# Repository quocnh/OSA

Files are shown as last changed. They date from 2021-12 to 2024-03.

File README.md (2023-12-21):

# ESP32_MedicalDevice
IoT devices to collect SPo2 and ECG for cancer treatment.

Downloading Repo from Github
---------------------------------------------------------------------------------------------------------------------------
- 1.) Navigate to "https://github.com/quocnh/OSA_Medical_Devices"
- 2.) Copy HTTPS link
- 3.) Open Git Bash in a local folder
- 4.) enter "git clone <Insert HTTP link here>"
---------------------------------------------------------------------------------------------------------------------------

Installing Firmware to ESP32
---------------------------------------------------------------------------------------------------------------------------
- 1.) Add ESP32 boards to Arduino IDE
	-File -> Preferences 
	-Enter "https://dl.espressif.com/dl/package_esp32_index.json" into "Additional Board Manager URLs" field
	-Tools -> Board -> Boards Manager...
	-Find "esp32" and install version 1.05
- 2.) Add necessary libraries to Arduino IDE
	-Sketch -> Include Library -> Add .ZIP library
	-Select .ZIP from "libraries" folder
	-Repeat for all libraries in the "libraries" folder

   	ArduinoHtppClient (0.5.0)
  	NTPClient(3.2.1)
  	AduinoJson(6.21.4)
  	AutoConnect(1.4.2)
  	PageBuilder(1.5.6)
  	PubSubCleint(2.8)
  	TPBubSupClient(2.9.1)
  	Thingsboard(0.10.2)
  
- 3.) Upload sketch to ESP32
	-Tools -> Board -> ESP32 dev module
	-Tools -> upload speed -> 115200
	-Tools -> Port -> select your COM port
	(https://www.silabs.com/developers/usb-to-uart-bridge-vcp-drivers?tab=downloads) iff missing driver
	-upload (arrow symbol)
	-If connection doesn't work, close sketch, disconnect and reconnect USB, reopen sketch and upload
---------------------------------------------------------------------------------------------------------------------------

Opening Thingsboard Dashboard
---------------------------------------------------------------------------------------------------------------------------
- 1.) Open "http://134.129.97.131:8080/" and sign in
	-login: "tenant@thingsboard.org"
	-password: "tenant"
- 2.) Navigate to ESP32 dashboard
	-Dashboard groups -> ESP32 -> Devkit Test
---------------------------------------------------------------------------------------------------------------------------

WiFi Autoconnect
---------------------------------------------------------------------------------------------------------------------------
- 1.) Power on programmed device and connect to the SpO2ap/ECGap with the default password "12345678"
- 2.) Navigate to "192.168.10.101/_ac" with SpO2ap and "192.168.10.102/_ac" with ECGap on your mobile device's web browser
- 3.) Press settings icon
- 4.) Press menu icon
- 5.) Add wifi network credentials
- 6.) Device will now autoconnect to WiFi
---------------------------------------------------------------------------------------------------------------------------
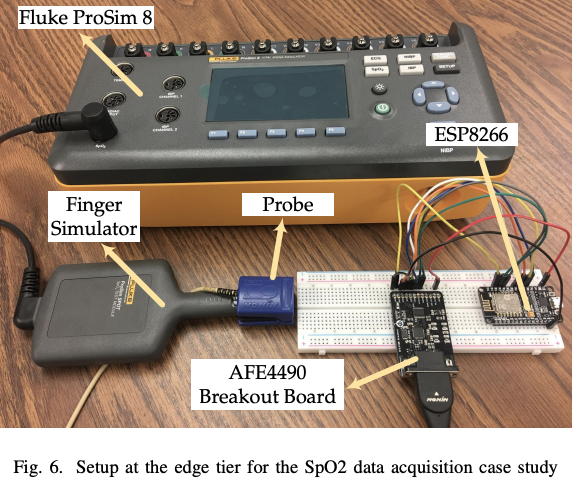
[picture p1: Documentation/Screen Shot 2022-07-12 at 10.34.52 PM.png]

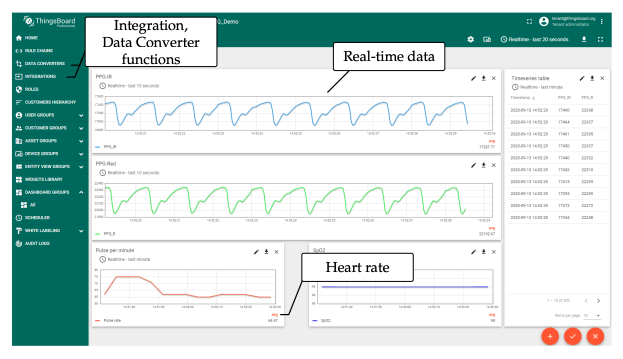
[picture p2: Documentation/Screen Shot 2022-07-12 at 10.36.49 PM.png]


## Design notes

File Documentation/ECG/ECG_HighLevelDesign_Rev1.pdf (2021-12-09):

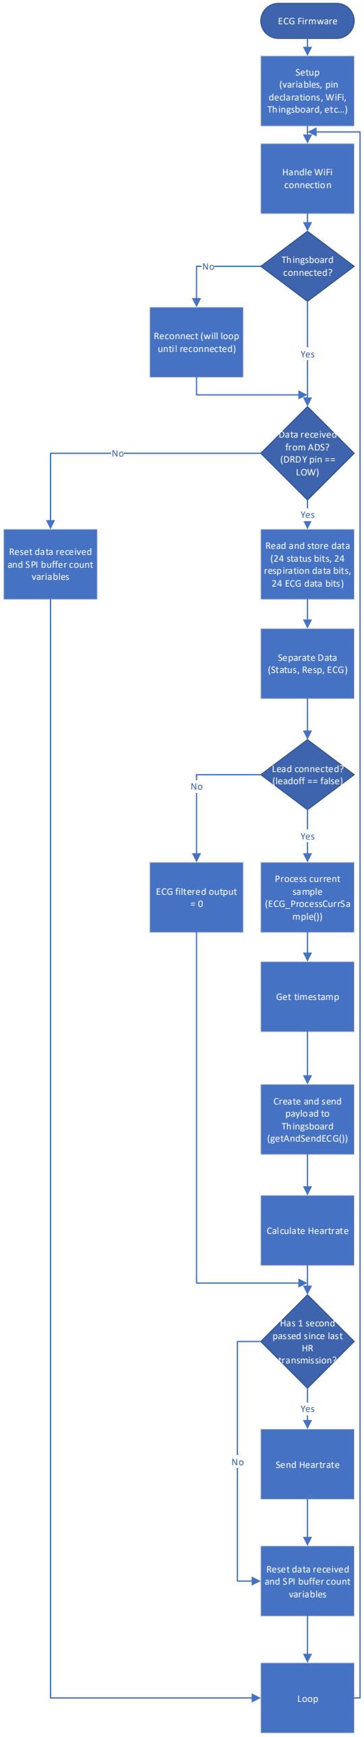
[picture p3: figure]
ECG Firmware; Setup (variables, pin declarations, WiFi, Thingsboard, etc…); Handle WiFi connection; Thingsboard connected?; Reconnect (will loop until reconnected); Data received from ADS? (DRDY pin == LOW); Yes; Read and store data (24 status bits, 24 respiration data bits, 24 ECG data bits); Reset data received and SPI buffer count variables; Separate Data (Status, Resp, ECG); Process current sample (ECG_ProcessCurrSa mple()); Get timestamp; Lead connected? (leadoff == false); Create and send payload to Thingsboard (getAndSendECG()); Calculate Heartrate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

Tom Hoskins – ECG Firmware high-level block diagram Rev 1 Arduino File: ESP32_to_Thingsboard.ino

Important configuration information

Pins:
ADS1292_DRDY_PIN = 4;
ADS1292_CS_PIN = 15;
ADS1292_START_PIN = 0;
ADS1292_PWDN_PIN = 2;

Sampling Rate: 250 SPS

Digital Filter:
40Hz LowPass
161 Order

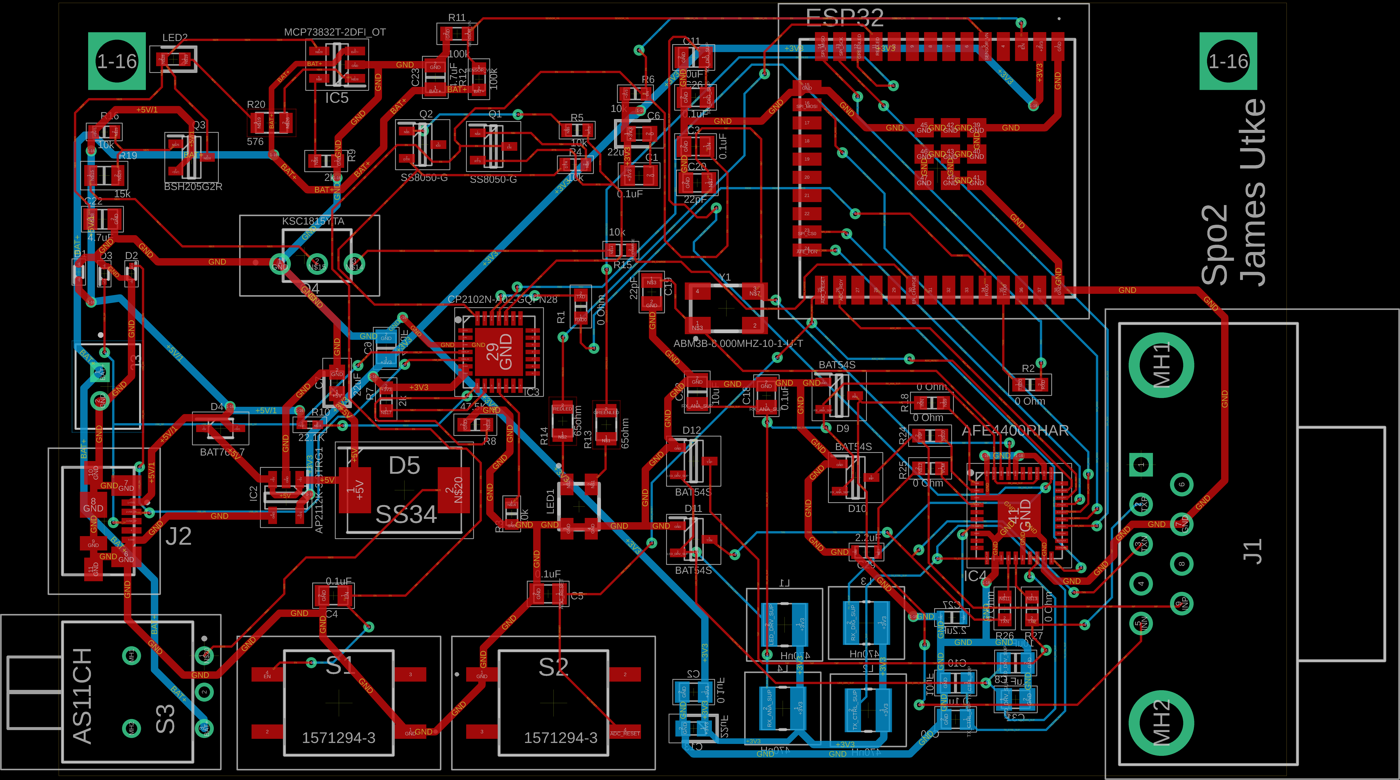
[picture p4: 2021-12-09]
Documentation/SPO2/SPo2_Rev.png

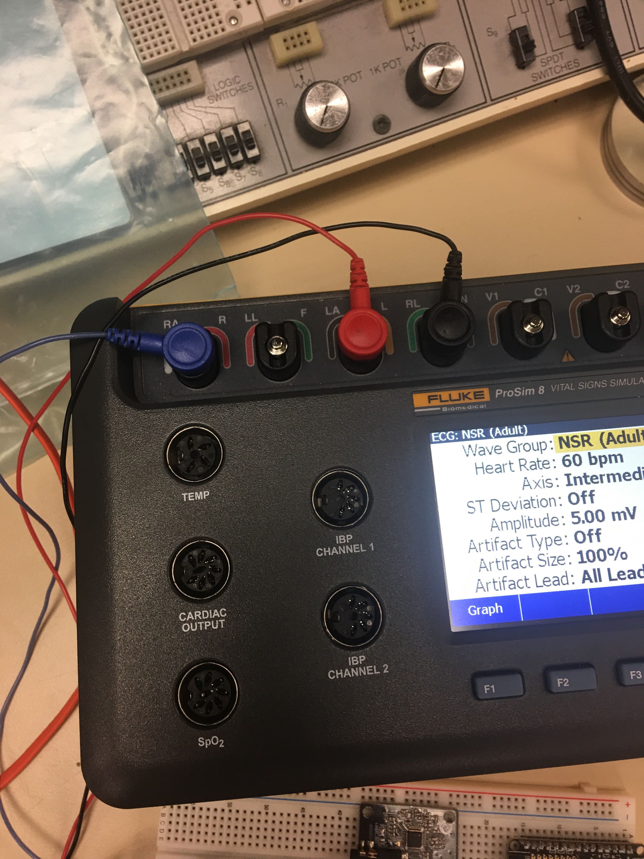
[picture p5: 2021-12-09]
Documentation/ECG/Image from iOS.jpg

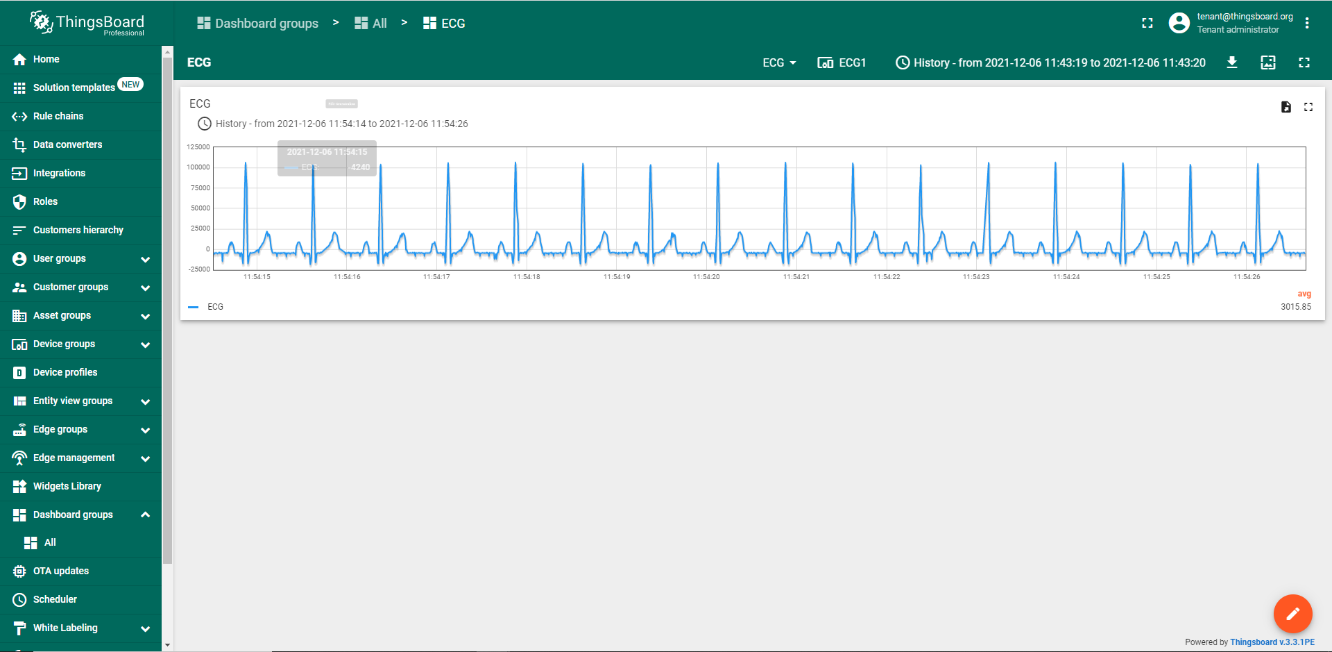
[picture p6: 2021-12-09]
Documentation/image.png

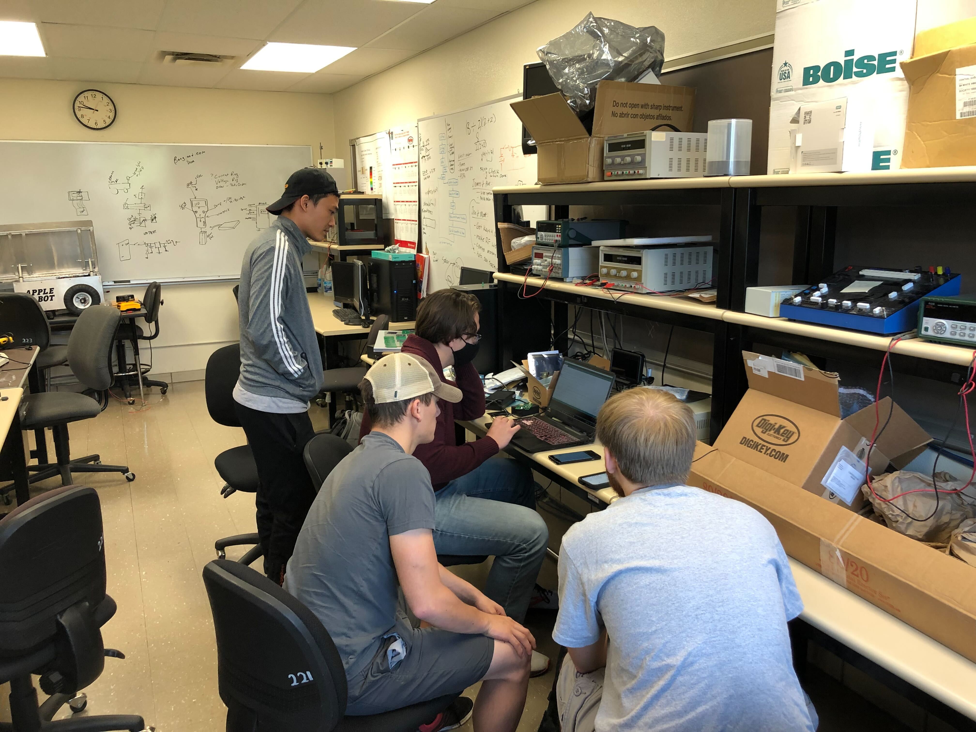
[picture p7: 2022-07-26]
Documentation/team.jpeg

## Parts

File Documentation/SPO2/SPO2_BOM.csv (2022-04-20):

Part | Value | Device | Package | Description | ARROW_PART_NUMBER | ARROW_PRICE-STOCK | DESCRIPTION | DIGI-KEY_PART_NUMBER | HEIGHT | MANUFACTURER_NAME | MANUFACTURER_PART_NUMBER | MF | MOUSER_PART_NUMBER | MOUSER_PRICE-STOCK | MP | PACKAGE | PURCHASE-URL | VALUE
C1 | 0.1uF | C0805C104K5RAC7411 | CAPC2012X88N | Cap Ceramic 0.1uF 50V X7R 10% Pad SMD 0805 125C T/R |  |  | Cap Ceramic 0.1uF 50V X7R 10% Pad SMD 0805 125C T/R |  | 0.88mm | Kemet | C0805C104K5RAC7411 |  | 80-C0805C104K5RACLR | https://www.mouser.co.uk/ProductDetail/KEMET/C0805C104K5RAC7411/?qs=jbRM9o5BbzPcVXF0wW9AYg%3D%3D |  |  |  | 0.1uF
C2 | 0.1uF | C0805C104K5RAC7411 | CAPC2012X88N | Cap Ceramic 0.1uF 50V X7R 10% Pad SMD 0805 125C T/R |  |  | Cap Ceramic 0.1uF 50V X7R 10% Pad SMD 0805 125C T/R |  | 0.88mm | Kemet | C0805C104K5RAC7411 |  | 80-C0805C104K5RACLR | https://www.mouser.co.uk/ProductDetail/KEMET/C0805C104K5RAC7411/?qs=jbRM9o5BbzPcVXF0wW9AYg%3D%3D |  |  |  | 0.1uF
C3 | 0.1uF | C0805C104K5RAC7411 | CAPC2012X88N | Cap Ceramic 0.1uF 50V X7R 10% Pad SMD 0805 125C T/R |  |  | Cap Ceramic 0.1uF 50V X7R 10% Pad SMD 0805 125C T/R |  | 0.88mm | Kemet | C0805C104K5RAC7411 |  | 80-C0805C104K5RACLR | https://www.mouser.co.uk/ProductDetail/KEMET/C0805C104K5RAC7411/?qs=jbRM9o5BbzPcVXF0wW9AYg%3D%3D |  |  |  | 0.1uF
C4 | 0.1uF | C0805C104K5RAC7411 | CAPC2012X88N | Cap Ceramic 0.1uF 50V X7R 10% Pad SMD 0805 125C T/R |  |  | Cap Ceramic 0.1uF 50V X7R 10% Pad SMD 0805 125C T/R |  | 0.88mm | Kemet | C0805C104K5RAC7411 |  | 80-C0805C104K5RACLR | https://www.mouser.co.uk/ProductDetail/KEMET/C0805C104K5RAC7411/?qs=jbRM9o5BbzPcVXF0wW9AYg%3D%3D |  |  |  | 0.1uF
C5 | 0.1uF | C0805C104K5RAC7411 | CAPC2012X88N | Cap Ceramic 0.1uF 50V X7R 10% Pad SMD 0805 125C T/R |  |  | Cap Ceramic 0.1uF 50V X7R 10% Pad SMD 0805 125C T/R |  | 0.88mm | Kemet | C0805C104K5RAC7411 |  | 80-C0805C104K5RACLR | https://www.mouser.co.uk/ProductDetail/KEMET/C0805C104K5RAC7411/?qs=jbRM9o5BbzPcVXF0wW9AYg%3D%3D |  |  |  | 0.1uF
C6 | 22uF | F381A226MMAAXE | CAPPC1609X90N | 22uF F38 Series Conductive Polymer, Miniature, Undertab Solid Electrolytic Chip Capacitors |  |  | 22uF F38 Series Conductive Polymer, Miniature, Undertab Solid Electrolytic Chip Capacitors |  | 0.9mm | AVX | F381A226MMAAXE |  | 581-F381A226MMAAXE | https://www.mouser.co.uk/ProductDetail/AVX/F381A226MMAAXE?qs=gTYE2QTfZfQFi8JvXKXiKg%3D%3D |  |  |  | 22uF
C7 | 22uF | F381A226MMAAXE | CAPPC1609X90N | 22uF F38 Series Conductive Polymer, Miniature, Undertab Solid Electrolytic Chip Capacitors |  |  | 22uF F38 Series Conductive Polymer, Miniature, Undertab Solid Electrolytic Chip Capacitors |  | 0.9mm | AVX | F381A226MMAAXE |  | 581-F381A226MMAAXE | https://www.mouser.co.uk/ProductDetail/AVX/F381A226MMAAXE?qs=gTYE2QTfZfQFi8JvXKXiKg%3D%3D |  |  |  | 22uF
C8 | 10uF | TMK212BC6106KG-T | CAPC2114X145N@1 | Status\tMass Production (Preferred) Capacitance\t10 uF +/- 10 % Case Size (EIA/JIS)\t0805/2012 Rated Voltage\t25 V tan (max)\t10 % Temperature Characteristic (EIA)\tX6S Operating Temp. Range (EIA)\t-55 to +105 High Temperature Loading (% Rated Voltage)\t150 % Insulation Resistance (min)\t100 MuF Dimension L\t2.0 +0.20/-0.00 mm Dimension W\t1.25 +0.20/-0.00 mm Dimension T\t1.25 +0.20/-0.00 mm Dimension e\t0.50 +/-0.25 mm RoHS Compliance (10 subst.)\tYes REACH Compliance (205 subst.)\tYes IEC62474 (Ver. D19 |  |  | Status Mass Production (Preferred) Capacitance 10 uF +/- 10 % Case Size (EIA/JIS) 0805/2012 Rated Voltage 25 V tan (max) 10 % Temperature Characteristic (EIA) X6S Operating Temp. Range (EIA) -55 to +105 High Temperature Loading (% Rated Voltage) 150 % Insulation Resistance (min) 100 MuF Dimension L 2.0 +0.20/-0.00 mm Dimension W 1.25 +0.20/-0.00 mm Dimension T 1.25 +0.20/-0.00 mm Dimension e 0.50 +/-0.25 mm RoHS Compliance (10 subst.) Yes REACH Compliance (205 subst.) Yes IEC62474 (Ver. D19 |  | 1.45mm | TAIYO YUDEN | TMK212BC6106KG-T |  | 963-TMK212BC6106KG-T | https://www.mouser.co.uk/ProductDetail/Taiyo-Yuden/TMK212BC6106KG-T/?qs=rI7uf1IzohRW7kV5WJ6mlg%3D%3D
C9 | 4.7uF | JMK212B7475KGHT | CAPC2114X145N | Taiyo Yuden JMK212B7475KGHT 4.7F MLCC 6.3V dc +/-10% Tolerance SMD |  |  | Taiyo Yuden JMK212B7475KGHT 4.7F MLCC 6.3V dc +/-10% Tolerance SMD |  | 1.45mm | TAIYO YUDEN | JMK212B7475KGHT |  | 963-JMK212B7475KGHT | https://www.mouser.co.uk/ProductDetail/Taiyo-Yuden/JMK212B7475KGHT/?qs=vmHwEFxEFR9NgetR%2FORAvw%3D%3D |  |  |  | 4.7uF
C10 | 10uF | TMK212BC6106KG-T | CAPC2114X145N@1 | Status\tMass Production (Preferred) Capacitance\t10 uF +/- 10 % Case Size (EIA/JIS)\t0805/2012 Rated Voltage\t25 V tan (max)\t10 % Temperature Characteristic (EIA)\tX6S Operating Temp. Range (EIA)\t-55 to +105 High Temperature Loading (% Rated Voltage)\t150 % Insulation Resistance (min)\t100 MuF Dimension L\t2.0 +0.20/-0.00 mm Dimension W\t1.25 +0.20/-0.00 mm Dimension T\t1.25 +0.20/-0.00 mm Dimension e\t0.50 +/-0.25 mm RoHS Compliance (10 subst.)\tYes REACH Compliance (205 subst.)\tYes IEC62474 (Ver. D19 |  |  | Status Mass Production (Preferred) Capacitance 10 uF +/- 10 % Case Size (EIA/JIS) 0805/2012 Rated Voltage 25 V tan (max) 10 % Temperature Characteristic (EIA) X6S Operating Temp. Range (EIA) -55 to +105 High Temperature Loading (% Rated Voltage) 150 % Insulation Resistance (min) 100 MuF Dimension L 2.0 +0.20/-0.00 mm Dimension W 1.25 +0.20/-0.00 mm Dimension T 1.25 +0.20/-0.00 mm Dimension e 0.50 +/-0.25 mm RoHS Compliance (10 subst.) Yes REACH Compliance (205 subst.) Yes IEC62474 (Ver. D19 |  | 1.45mm | TAIYO YUDEN | TMK212BC6106KG-T |  | 963-TMK212BC6106KG-T | https://www.mouser.co.uk/ProductDetail/Taiyo-Yuden/TMK212BC6106KG-T/?qs=rI7uf1IzohRW7kV5WJ6mlg%3D%3D
C11 | 10uF | TMK212BC6106KG-T | CAPC2114X145N@1 | Status\tMass Production (Preferred) Capacitance\t10 uF +/- 10 % Case Size (EIA/JIS)\t0805/2012 Rated Voltage\t25 V tan (max)\t10 % Temperature Characteristic (EIA)\tX6S Operating Temp. Range (EIA)\t-55 to +105 High Temperature Loading (% Rated Voltage)\t150 % Insulation Resistance (min)\t100 MuF Dimension L\t2.0 +0.20/-0.00 mm Dimension W\t1.25 +0.20/-0.00 mm Dimension T\t1.25 +0.20/-0.00 mm Dimension e\t0.50 +/-0.25 mm RoHS Compliance (10 subst.)\tYes REACH Compliance (205 subst.)\tYes IEC62474 (Ver. D19 |  |  | Status Mass Production (Preferred) Capacitance 10 uF +/- 10 % Case Size (EIA/JIS) 0805/2012 Rated Voltage 25 V tan (max) 10 % Temperature Characteristic (EIA) X6S Operating Temp. Range (EIA) -55 to +105 High Temperature Loading (% Rated Voltage) 150 % Insulation Resistance (min) 100 MuF Dimension L 2.0 +0.20/-0.00 mm Dimension W 1.25 +0.20/-0.00 mm Dimension T 1.25 +0.20/-0.00 mm Dimension e 0.50 +/-0.25 mm RoHS Compliance (10 subst.) Yes REACH Compliance (205 subst.) Yes IEC62474 (Ver. D19 |  | 1.45mm | TAIYO YUDEN | TMK212BC6106KG-T |  | 963-TMK212BC6106KG-T | https://www.mouser.co.uk/ProductDetail/Taiyo-Yuden/TMK212BC6106KG-T/?qs=rI7uf1IzohRW7kV5WJ6mlg%3D%3D
C12 | 10uF | TMK212BC6106KG-T | CAPC2114X145N@1 | Status\tMass Production (Preferred) Capacitance\t10 uF +/- 10 % Case Size (EIA/JIS)\t0805/2012 Rated Voltage\t25 V tan (max)\t10 % Temperature Characteristic (EIA)\tX6S Operating Temp. Range (EIA)\t-55 to +105 High Temperature Loading (% Rated Voltage)\t150 % Insulation Resistance (min)\t100 MuF Dimension L\t2.0 +0.20/-0.00 mm Dimension W\t1.25 +0.20/-0.00 mm Dimension T\t1.25 +0.20/-0.00 mm Dimension e\t0.50 +/-0.25 mm RoHS Compliance (10 subst.)\tYes REACH Compliance (205 subst.)\tYes IEC62474 (Ver. D19 |  |  | Status Mass Production (Preferred) Capacitance 10 uF +/- 10 % Case Size (EIA/JIS) 0805/2012 Rated Voltage 25 V tan (max) 10 % Temperature Characteristic (EIA) X6S Operating Temp. Range (EIA) -55 to +105 High Temperature Loading (% Rated Voltage) 150 % Insulation Resistance (min) 100 MuF Dimension L 2.0 +0.20/-0.00 mm Dimension W 1.25 +0.20/-0.00 mm Dimension T 1.25 +0.20/-0.00 mm Dimension e 0.50 +/-0.25 mm RoHS Compliance (10 subst.) Yes REACH Compliance (205 subst.) Yes IEC62474 (Ver. D19 |  | 1.45mm | TAIYO YUDEN | TMK212BC6106KG-T |  | 963-TMK212BC6106KG-T | https://www.mouser.co.uk/ProductDetail/Taiyo-Yuden/TMK212BC6106KG-T/?qs=rI7uf1IzohRW7kV5WJ6mlg%3D%3D
C13 | 22uF | F381A226MMAAXE | CAPPC1609X90N | 22uF F38 Series Conductive Polymer, Miniature, Undertab Solid Electrolytic Chip Capacitors |  |  | 22uF F38 Series Conductive Polymer, Miniature, Undertab Solid Electrolytic Chip Capacitors |  | 0.9mm | AVX | F381A226MMAAXE |  | 581-F381A226MMAAXE | https://www.mouser.co.uk/ProductDetail/AVX/F381A226MMAAXE?qs=gTYE2QTfZfQFi8JvXKXiKg%3D%3D |  |  |  | 22uF
C18 | 0.1uF | C0805C104K5RAC7411 | CAPC2012X88N | Cap Ceramic 0.1uF 50V X7R 10% Pad SMD 0805 125C T/R |  |  | Cap Ceramic 0.1uF 50V X7R 10% Pad SMD 0805 125C T/R |  | 0.88mm | Kemet | C0805C104K5RAC7411 |  | 80-C0805C104K5RACLR | https://www.mouser.co.uk/ProductDetail/KEMET/C0805C104K5RAC7411/?qs=jbRM9o5BbzPcVXF0wW9AYg%3D%3D |  |  |  | 0.1uF
C19 | 22pF | C0805C220K1HACTU | CAPC2012X88N@1 | Multilayer Ceramic Capacitors MLCC - SMD/SMT 100V 22pF X8R 0805 10% |  |  | Multilayer Ceramic Capacitors MLCC - SMD/SMT 100V 22pF X8R 0805 10% |  | 0.88mm | Kemet | C0805C220K1HACTU |  | 80-C0805C220K1HACTU | https://www.mouser.co.uk/ProductDetail/KEMET/C0805C220K1HACTU/?qs=W0yvOO0ixfHaPTgNXyVDyQ%3D%3D
C20 | 22pF | C0805C220K1HACTU | CAPC2012X88N@1 | Multilayer Ceramic Capacitors MLCC - SMD/SMT 100V 22pF X8R 0805 10% |  |  | Multilayer Ceramic Capacitors MLCC - SMD/SMT 100V 22pF X8R 0805 10% |  | 0.88mm | Kemet | C0805C220K1HACTU |  | 80-C0805C220K1HACTU | https://www.mouser.co.uk/ProductDetail/KEMET/C0805C220K1HACTU/?qs=W0yvOO0ixfHaPTgNXyVDyQ%3D%3D
C22 | 4.7uF | JMK212B7475KGHT | CAPC2114X145N | Taiyo Yuden JMK212B7475KGHT 4.7F MLCC 6.3V dc +/-10% Tolerance SMD |  |  | Taiyo Yuden JMK212B7475KGHT 4.7F MLCC 6.3V dc +/-10% Tolerance SMD |  | 1.45mm | TAIYO YUDEN | JMK212B7475KGHT |  | 963-JMK212B7475KGHT | https://www.mouser.co.uk/ProductDetail/Taiyo-Yuden/JMK212B7475KGHT/?qs=vmHwEFxEFR9NgetR%2FORAvw%3D%3D |  |  |  | 4.7uF
C23 | 4.7uF | JMK212B7475KGHT | CAPC2114X145N | Taiyo Yuden JMK212B7475KGHT 4.7F MLCC 6.3V dc +/-10% Tolerance SMD |  |  | Taiyo Yuden JMK212B7475KGHT 4.7F MLCC 6.3V dc +/-10% Tolerance SMD |  | 1.45mm | TAIYO YUDEN | JMK212B7475KGHT |  | 963-JMK212B7475KGHT | https://www.mouser.co.uk/ProductDetail/Taiyo-Yuden/JMK212B7475KGHT/?qs=vmHwEFxEFR9NgetR%2FORAvw%3D%3D |  |  |  | 4.7uF
C26 | 0.1uF | C0805C104K5RAC7411 | CAPC2012X88N | Cap Ceramic 0.1uF 50V X7R 10% Pad SMD 0805 125C T/R |  |  | Cap Ceramic 0.1uF 50V X7R 10% Pad SMD 0805 125C T/R |  | 0.88mm | Kemet | C0805C104K5RAC7411 |  | 80-C0805C104K5RACLR | https://www.mouser.co.uk/ProductDetail/KEMET/C0805C104K5RAC7411/?qs=jbRM9o5BbzPcVXF0wW9AYg%3D%3D |  |  |  | 0.1uF
C27 | 2.2uF | C1608X7S1C225K080AE | CAPC1608X80N | Multilayer Ceramic Capacitors MLCC - SMD/SMT 0603 16VDC 2.2uF 10% X7S |  |  | Multilayer Ceramic Capacitors MLCC - SMD/SMT 0603 16VDC 2.2uF 10% X7S |  | 0.8mm | TDK | C1608X7S1C225K080AE |  | 810-C1608X7S1C225K08 | https://www.mouser.co.uk/ProductDetail/TDK/C1608X7S1C225K080AE/?qs=zW32dvEIR3tqedNHz865EA%3D%3D |  |  |  | 2.2uF
C29 | 2.2uF | C1608X7S1C225K080AE | CAPC1608X80N | Multilayer Ceramic Capacitors MLCC - SMD/SMT 0603 16VDC 2.2uF 10% X7S |  |  | Multilayer Ceramic Capacitors MLCC - SMD/SMT 0603 16VDC 2.2uF 10% X7S |  | 0.8mm | TDK | C1608X7S1C225K080AE |  | 810-C1608X7S1C225K08 | https://www.mouser.co.uk/ProductDetail/TDK/C1608X7S1C225K080AE/?qs=zW32dvEIR3tqedNHz865EA%3D%3D |  |  |  | 2.2uF
C30 | 0.1uF | C0805C104K5RAC7411 | CAPC2012X88N | Cap Ceramic 0.1uF 50V X7R 10% Pad SMD 0805 125C T/R |  |  | Cap Ceramic 0.1uF 50V X7R 10% Pad SMD 0805 125C T/R |  | 0.88mm | Kemet | C0805C104K5RAC7411 |  | 80-C0805C104K5RACLR | https://www.mouser.co.uk/ProductDetail/KEMET/C0805C104K5RAC7411/?qs=jbRM9o5BbzPcVXF0wW9AYg%3D%3D |  |  |  | 0.1uF
C31 | 1uF | C0805X105K8RAC7210 | CAPC2012X100N | Multilayer Ceramic Capacitors MLCC - SMD/SMT 10V 1uF X7R 0805 10% Flex |  |  | Multilayer Ceramic Capacitors MLCC - SMD/SMT 10V 1uF X7R 0805 10% Flex |  | 1mm | Kemet | C0805X105K8RAC7210 |  | 80-C0805X105K8RACLR | https://www.mouser.co.uk/ProductDetail/KEMET/C0805X105K8RAC7210?qs=ds50AKTGxA8Ac4j4qbsB5A%3D%3D
D1 | CPDQ5V0-HF | CPDQ5V0-HF | SODFL1006X40N | ESD Suppressors / TVS Diodes SMD ESD Diode 5V Bi-Direction |  |  | ESD Suppressors / TVS Diodes SMD ESD Diode 5V Bi-Direction |  | 0.4mm | Comchip Technology | CPDQ5V0-HF |  | 750-CPDQ5V0-HF | https://www.mouser.co.uk/ProductDetail/Comchip-Technology/CPDQ5V0-HF/?qs=ccyN4P6STah119k8k5VB0Q%3D%3D
D2 | CPDQ5V0-HF | CPDQ5V0-HF | SODFL1006X40N | ESD Suppressors / TVS Diodes SMD ESD Diode 5V Bi-Direction |  |  | ESD Suppressors / TVS Diodes SMD ESD Diode 5V Bi-Direction |  | 0.4mm | Comchip Technology | CPDQ5V0-HF |  | 750-CPDQ5V0-HF | https://www.mouser.co.uk/ProductDetail/Comchip-Technology/CPDQ5V0-HF/?qs=ccyN4P6STah119k8k5VB0Q%3D%3D
D3 | CPDQ5V0-HF | CPDQ5V0-HF | SODFL1006X40N | ESD Suppressors / TVS Diodes SMD ESD Diode 5V Bi-Direction |  |  | ESD Suppressors / TVS Diodes SMD ESD Diode 5V Bi-Direction |  | 0.4mm | Comchip Technology | CPDQ5V0-HF |  | 750-CPDQ5V0-HF | https://www.mouser.co.uk/ProductDetail/Comchip-Technology/CPDQ5V0-HF/?qs=ccyN4P6STah119k8k5VB0Q%3D%3D
D4 | BAT760-7 | BAT760-7 | SOD2513X120N | Diode Schottky 30V 1A 2Pin SOD323 Diodes Inc BAT760-7, SMT Schottky Diode, 30V 1A, 2-Pin SOD-323 |  |  | Diode Schottky 30V 1A 2Pin SOD323 Diodes Inc BAT760-7, SMT Schottky Diode, 30V 1A, 2-Pin SOD-323 |  | 1.2mm | Diodes Inc. | BAT760-7 |  | 621-BAT760-7 | https://www.mouser.co.uk/ProductDetail/Diodes-Incorporated/BAT760-7?qs=JV7lzlMm3yKDDyO09xoRbQ%3D%3D
D5 | SS34 | SS34 | DIOM8059X256N | ON Semi SS34 SMT Schottky Diode, 40V 3A, 2-Pin DO-214AB |  |  | ON Semi SS34 SMT Schottky Diode, 40V 3A, 2-Pin DO-214AB |  | 2.56mm | ON Semiconductor | SS34 |  | 512-SS34 | https://www.mouser.co.uk/ProductDetail/ON-Semiconductor-Fairchild/SS34?qs=2ONuHmP%2FXzb3ub11UdFfdQ%3D%3D
D9 | BAT54S | BAT54S | SOT95P240X110-3N | Schottky Diodes & Rectifiers SOT23 0.2A 30V Schot tky Dblr |  |  | Schottky Diodes & Rectifiers SOT23 0.2A 30V Schot tky Dblr |  | 1.1mm | Rectron | BAT54S |  | 583-BAT54S | https://www.mouser.co.uk/ProductDetail/Rectron/BAT54S/?qs=7pEAo90IqNGRiqD7TkybWA%3D%3D
D10 | BAT54S | BAT54S | SOT95P240X110-3N | Schottky Diodes & Rectifiers SOT23 0.2A 30V Schot tky Dblr |  |  | Schottky Diodes & Rectifiers SOT23 0.2A 30V Schot tky Dblr |  | 1.1mm | Rectron | BAT54S |  | 583-BAT54S | https://www.mouser.co.uk/ProductDetail/Rectron/BAT54S/?qs=7pEAo90IqNGRiqD7TkybWA%3D%3D
D11 | BAT54S | BAT54S | SOT95P240X110-3N | Schottky Diodes & Rectifiers SOT23 0.2A 30V Schot tky Dblr |  |  | Schottky Diodes & Rectifiers SOT23 0.2A 30V Schot tky Dblr |  | 1.1mm | Rectron | BAT54S |  | 583-BAT54S | https://www.mouser.co.uk/ProductDetail/Rectron/BAT54S/?qs=7pEAo90IqNGRiqD7TkybWA%3D%3D
D12 | BAT54S | BAT54S | SOT95P240X110-3N | Schottky Diodes & Rectifiers SOT23 0.2A 30V Schot tky Dblr |  |  | Schottky Diodes & Rectifiers SOT23 0.2A 30V Schot tky Dblr |  | 1.1mm | Rectron | BAT54S |  | 583-BAT54S | https://www.mouser.co.uk/ProductDetail/Rectron/BAT54S/?qs=7pEAo90IqNGRiqD7TkybWA%3D%3D
IC1 | ESP32-WROOM-32D_M113DH2800PH3Q | ESP32-WROOM-32D_M113DH2800PH3Q | ESP32WROOM32DM113DH2800PH3Q0 | WiFi Modules (802.11) SMD Module, ESP32-D0WD, 32Mbits SPI flash, UART mode, PCB antenna |  |  | WiFi Modules (802.11) SMD Module, ESP32-D0WD, 32Mbits SPI flash, UART mode, PCB antenna |  | 3.2mm | Espressif Systems | ESP32-WROOM-32D(M113DH2800PH3Q0) |  | 356-ES32WROOM32D16MB | https://www.mouser.co.uk/ProductDetail/Espressif-Systems/ESP32-WROOM-32DM113DH2800PH3Q0/?qs=W%2FMpXkg%252BdQ75%2Fda1rSxxJw%3D%3D
IC2 | AP2112K-3.3TRG1 | AP2112K-3.3TRG1 | SOT95P282X130-5N | 600mA 3.3V LDO Regulator Enable SOT23-5 DiodesZetex AP2112K-3.3TRG1, LDO Voltage Regulator, 3.3 V +/-1.5%, 2.5 6 Vin, 5-Pin SOT-23 |  |  | 600mA 3.3V LDO Regulator Enable SOT23-5 DiodesZetex AP2112K-3.3TRG1, LDO Voltage Regulator, 3.3 V +/-1.5%, 2.5 6 Vin, 5-Pin SOT-23 |  | 1.3mm | Diodes Inc. | AP2112K-3.3TRG1 |  | 621-AP2112K-3.3TRG1 | https://www.mouser.co.uk/ProductDetail/Diodes-Incorporated/AP2112K-33TRG1/?qs=x6A8l6qLYDDPYHosCdzh%2FA%3D%3D
IC3 | CP2102N-A02-GQFN28 | CP2102N-A02-GQFN28 | QFN50P500X500X80-29N | SILICON LABS - CP2102N-A02-GQFN28 - USB TO UART BRIDGE, -40 TO 85DEG C |  |  | SILICON LABS - CP2102N-A02-GQFN28 - USB TO UART BRIDGE, -40 TO 85DEG C |  | 0.8mm | Silicon Labs | CP2102N-A02-GQFN28 |  | 634-CP2102NA02GQFN28 | https://www.mouser.co.uk/ProductDetail/Silicon-Labs/CP2102N-A02-GQFN28/?qs=u16ybLDytRaSBkSkyjYFiA%3D%3D
IC4 | AFE4400RHAR | AFE4400RHAR | QFN50P600X600X100-41N | Integrated Analog Front End (AFE) for Heart-Rate Monitors and Low-Cost Pulse Oximeters |  |  | Integrated Analog Front End (AFE) for Heart-Rate Monitors and Low-Cost Pulse Oximeters |  | 1mm | Texas Instruments | AFE4400RHAR |  | 595-AFE4400RHAR | https://www.mouser.co.uk/ProductDetail/Texas-Instruments/AFE4400RHAR/?qs=MURVExHfc2zl%2FM9SqCv0pw%3D%3D
IC5 | MCP73832T-2DFI_OT | MCP73832T-2DFI_OT | SOT95P270X145-5N | Battery Management 4.2V Li-Ion/Li-Poly Chrg mgnt controller |  |  | Battery Management 4.2V Li-Ion/Li-Poly Chrg mgnt controller |  | 1.45mm | Microchip | MCP73832T-2DFI/OT |  | 579-MCP73832T2DFI/OT | https://www.mouser.co.uk/ProductDetail/Microchip-Technology/MCP73832T-2DFI-OT?qs=Of9BA0M78V%2Fd7MaXZyVc5w%3D%3D
J1 | 1734035-3 | 1734035-3 | 17340353 | USB Connectors Mini R/A SMT B Type |  |  | USB Connectors Mini R/A SMT B Type |  | 3.95mm | TE Connectivity | 1734035-3 |  | 571-1734035-3 | https://www.mouser.co.uk/ProductDetail/TE-Connectivity/1734035-3?qs=JQ0T48ZyHbB%2Fl8a%2FPKP6Xw%3D%3D
J2 | 47346-1001 | 47346-1001 | 473461001 | MOLEX - 47346-1001 - MULTIPOLE CONNECTOR |  |  | MOLEX - 47346-1001 - MULTIPOLE CONNECTOR |  | 2.94mm | Molex | 47346-1001 |  | 538-47346-1001 | https://www.mouser.co.uk/ProductDetail/Molex/47346-1001/?qs=yd8XiKYcH9muPqUKe4E0Dw%3D%3D
J3 | B2B-PH-K-S(LF)(SN) | B2B-PH-K-S(LF)(SN) | JST_B2B-PH-K-S(LF)(SN) | PH Series 2 Position 2 mm Pitch Through Hole Top Entry Shrouded Header |  |  | Connector Header Through Hole 2 position 0.079 (2.00mm) | 455-1704-ND |  |  |  | JST Sales |  |  | B2B-PH-K-S(LF)(SN) | None | https://pricing.snapeda.com/search/part/B2B-PH-K-S(LF)(SN)/?ref=eda
L1 | 470nH | LPS3010-471MRC | LPS3010471MRC | Fixed Inductors 470nH Shld 1.8A 70 mOhms AECQ2 |  |  | Fixed Inductors 470nH Shld 1.8A 70 mOhms AECQ2 |  | 1mm | COILCRAFT | LPS3010-471MRC
L2 | 470nH | LPS3010-471MRC | LPS3010471MRC | Fixed Inductors 470nH Shld 1.8A 70 mOhms AECQ2 |  |  | Fixed Inductors 470nH Shld 1.8A 70 mOhms AECQ2 |  | 1mm | COILCRAFT | LPS3010-471MRC
L3 | 470nH | LPS3010-471MRC | LPS3010471MRC | Fixed Inductors 470nH Shld 1.8A 70 mOhms AECQ2 |  |  | Fixed Inductors 470nH Shld 1.8A 70 mOhms AECQ2 |  | 1mm | COILCRAFT | LPS3010-471MRC
L4 | 470nH | LPS3010-471MRC | LPS3010471MRC | Fixed Inductors 470nH Shld 1.8A 70 mOhms AECQ2 |  |  | Fixed Inductors 470nH Shld 1.8A 70 mOhms AECQ2 |  | 1mm | COILCRAFT | LPS3010-471MRC
LED1 | 150141RV73100 | 150141RV73100 | SMD3528_1 | LED,Wurth Elektronik,150141RV73100 Wurth Elektronik 150141RV73100, WL-SBTW Series Bi-colour Green, Red LED, 572 / 625 nm 4-Pin 3528 (1411), Round Lens |  |  | LED,Wurth Elektronik,150141RV73100 Wurth Elektronik 150141RV73100, WL-SBTW Series Bi-colour Green, Red LED, 572 / 625 nm 4-Pin 3528 (1411), Round Lens |  | mm | Wurth Elektronik | 150141RV73100 |  | 710-150141RV73100 | https://www.mouser.co.uk/ProductDetail/Wurth-Elektronik/150141RV73100?qs=LlUlMxKIyB1w9QlMugtMLA%3D%3D
LED2 | LTST-C193KRKT-5A | LTST-C193KRKT-5A | LEDC1608X45N | Lite-On LTST-C193KRKT-5A, 631 nm Red LED, 1608 (0603) SMD package |  |  | Lite-On LTST-C193KRKT-5A, 631 nm Red LED, 1608 (0603) SMD package |  | 0.45mm | Lite-On | LTST-C193KRKT-5A |  | 859-LTSTC193KRKT5A | https://www.mouser.co.uk/ProductDetail/Lite-On/LTST-C193KRKT-5A/?qs=xIkB7y1OTor17kZSHyF5tQ%3D%3D
Q1 | SS8050-G | SS8050-G | SOT95P240X115-3N | Bipolar Transistors - BJT NPN TRANSISTOR 1.5A 40V |  |  | Bipolar Transistors - BJT NPN TRANSISTOR 1.5A 40V |  | 1.15mm | Comchip Technology | SS8050-G |  | 750-SS8050-G | https://www.mouser.co.uk/ProductDetail/Comchip-Technology/SS8050-G/?qs=LLUE9lz1YbcHg%252BWLMAtcrQ%3D%3D
Q2 | SS8050-G | SS8050-G | SOT95P240X115-3N | Bipolar Transistors - BJT NPN TRANSISTOR 1.5A 40V |  |  | Bipolar Transistors - BJT NPN TRANSISTOR 1.5A 40V |  | 1.15mm | Comchip Technology | SS8050-G |  | 750-SS8050-G | https://www.mouser.co.uk/ProductDetail/Comchip-Technology/SS8050-G/?qs=LLUE9lz1YbcHg%252BWLMAtcrQ%3D%3D
Q3 | BSH205G2R | BSH205G2R | SOT95P230X110-3N | MOSFET 20V P-channel Trench MOSFET |  |  | MOSFET 20V P-channel Trench MOSFET |  | 1.1mm | Nexperia | BSH205G2R |  | 771-BSH205G2R | https://www.mouser.co.uk/ProductDetail/Nexperia/BSH205G2R?qs=%252BRKXB2WKlScNIfK4SlBmFA%3D%3D
Q4 | KSC1815YTA | KSC1815YTA | BC33740TA | Transistor, Fairchild, KSC1815YTA |  |  | Transistor, Fairchild, KSC1815YTA |  | mm | ON Semiconductor | KSC1815YTA |  | 512-KSC1815YTA | https://www.mouser.co.uk/ProductDetail/ON-Semiconductor-Fairchild/KSC1815YTA?qs=ljbEvF4DwOP9FJQWOCoFLQ%3D%3D
R1 | 0 Ohm | CR0603AJ_-000ELF | RESC1608X55N | Thick Film Resistors - SMD ResA 0603 0R Jumper 100mW AEC-Q200 |  |  | Thick Film Resistors - SMD ResA 0603 0R Jumper 100mW AEC-Q200 |  | 0.55mm | Bourns | CR0603AJ/-000ELF |  | 652-CR0603AJ/-000ELF | https://www.mouser.co.uk/ProductDetail/Bourns/CR0603AJ-000ELF/?qs=GedFDFLaBXF8EepoWODZMQ%3D%3D |  |  |  | 0 Ohm
R2 | 0 Ohm | CR0603AJ_-000ELF | RESC1608X55N | Thick Film Resistors - SMD ResA 0603 0R Jumper 100mW AEC-Q200 |  |  | Thick Film Resistors - SMD ResA 0603 0R Jumper 100mW AEC-Q200 |  | 0.55mm | Bourns | CR0603AJ/-000ELF |  | 652-CR0603AJ/-000ELF | https://www.mouser.co.uk/ProductDetail/Bourns/CR0603AJ-000ELF/?qs=GedFDFLaBXF8EepoWODZMQ%3D%3D |  |  |  | 0 Ohm
R3 | 10k | HV73V1JTTD103J | CAPC1608X55N | Thick Film Resistors - SMD 10000Ohms 5% 0603 TCR=100 AEC-Q200 |  |  | Thick Film Resistors - SMD 10000Ohms 5% 0603 TCR=100 AEC-Q200 |  | 0.55mm | KOA Speer | HV73V1JTTD103J |  | 660-HV73V1JTTD103J | https://www.mouser.co.uk/ProductDetail/KOA-Speer/HV73V1JTTD103J?qs=xZ%2FP%252Ba9zWqbXuiWLWua7%2Fw%3D%3D |  |  |  | 10k
R4 | 10k | HV73V1JTTD103J | CAPC1608X55N | Thick Film Resistors - SMD 10000Ohms 5% 0603 TCR=100 AEC-Q200 |  |  | Thick Film Resistors - SMD 10000Ohms 5% 0603 TCR=100 AEC-Q200 |  | 0.55mm | KOA Speer | HV73V1JTTD103J |  | 660-HV73V1JTTD103J | https://www.mouser.co.uk/ProductDetail/KOA-Speer/HV73V1JTTD103J?qs=xZ%2FP%252Ba9zWqbXuiWLWua7%2Fw%3D%3D |  |  |  | 10k
R5 | 10k | HV73V1JTTD103J | CAPC1608X55N | Thick Film Resistors - SMD 10000Ohms 5% 0603 TCR=100 AEC-Q200 |  |  | Thick Film Resistors - SMD 10000Ohms 5% 0603 TCR=100 AEC-Q200 |  | 0.55mm | KOA Speer | HV73V1JTTD103J |  | 660-HV73V1JTTD103J | https://www.mouser.co.uk/ProductDetail/KOA-Speer/HV73V1JTTD103J?qs=xZ%2FP%252Ba9zWqbXuiWLWua7%2Fw%3D%3D |  |  |  | 10k
R6 | 10k | HV73V1JTTD103J | CAPC1608X55N | Thick Film Resistors - SMD 10000Ohms 5% 0603 TCR=100 AEC-Q200 |  |  | Thick Film Resistors - SMD 10000Ohms 5% 0603 TCR=100 AEC-Q200 |  | 0.55mm | KOA Speer | HV73V1JTTD103J |  | 660-HV73V1JTTD103J | https://www.mouser.co.uk/ProductDetail/KOA-Speer/HV73V1JTTD103J?qs=xZ%2FP%252Ba9zWqbXuiWLWua7%2Fw%3D%3D |  |  |  | 10k
R7 | 2k | ERJ-UP3F2001V | RESC1608X55N | Anti-Sulfurated Thick Film Chip Resistors / Anti-Surge Type |  |  | Anti-Sulfurated Thick Film Chip Resistors / Anti-Surge Type |  | 0.55mm | Panasonic | ERJ-UP3F2001V |  |  |  |  |  |  | 2k
R8 | 47.5K | ERJ-UP3F4752V | RESC1608X55N | Thick Film Resistors - SMD AEC-Q200 |  |  | Thick Film Resistors - SMD AEC-Q200 |  | 0.55mm | Panasonic | ERJ-UP3F4752V |  | 667-ERJ-UP3F4752V | https://www.mouser.co.uk/ProductDetail/Panasonic/ERJ-UP3F4752V?qs=GedFDFLaBXGUd1E4zR%252BF8g%3D%3D |  |  |  | 47.5K
R9 | 2k | ERJ-UP3F2001V | RESC1608X55N | Anti-Sulfurated Thick Film Chip Resistors / Anti-Surge Type |  |  | Anti-Sulfurated Thick Film Chip Resistors / Anti-Surge Type |  | 0.55mm | Panasonic | ERJ-UP3F2001V |  |  |  |  |  |  | 2k
R10 | 22.1K | ERJ-2RHD2212X | RESC1005X40N | Thick Film Resistors - SMD 0402 Resistor 0.5% 50ppm 22.1KOhm |  |  | Thick Film Resistors - SMD 0402 Resistor 0.5% 50ppm 22.1KOhm |  | 0.4mm | Panasonic | ERJ-2RHD2212X |  | 667-ERJ-2RHD2212X | https://www.mouser.co.uk/ProductDetail/Panasonic/ERJ-2RHD2212X?qs=pfd5qewlna6lhy494ElLrw%3D%3D |  |  |  | 22.1K
R11 | 100k | RCG0603100KJNEA | RESC1608X50N | RCG0603100KJNEA |  |  | RCG0603100KJNEA |  | 0.5mm | Vishay | RCG0603100KJNEA |  | 71-RCG0603100KJNEA | https://www.mouser.com/Search/Refine.aspx?Keyword=71-RCG0603100KJNEA |  |  |  | 100k
R12 | 100k | RCG0603100KJNEA | RESC1608X50N | RCG0603100KJNEA |  |  | RCG0603100KJNEA |  | 0.5mm | Vishay | RCG0603100KJNEA |  | 71-RCG0603100KJNEA | https://www.mouser.com/Search/Refine.aspx?Keyword=71-RCG0603100KJNEA |  |  |  | 100k
R13 | 65ohm | Y402265R0000A9W | RESC2012X64N |  |  |  | 65 Ohms ±0.05% 0.2W, 1/5W Chip Resistor 0805 (2012 Metric) Moisture Resistant, Non-Inductive Metal Foil | Y402265R0000A9W-ND |  |  |  | Vishay |  |  | Y402265R0000A9W | 2012 Vishay
R14 | 65ohm | Y402265R0000A9W | RESC2012X64N |  |  |  | 65 Ohms ±0.05% 0.2W, 1/5W Chip Resistor 0805 (2012 Metric) Moisture Resistant, Non-Inductive Metal Foil | Y402265R0000A9W-ND |  |  |  | Vishay |  |  | Y402265R0000A9W | 2012 Vishay
R15 | 10k | HV73V1JTTD103J | CAPC1608X55N | Thick Film Resistors - SMD 10000Ohms 5% 0603 TCR=100 AEC-Q200 |  |  | Thick Film Resistors - SMD 10000Ohms 5% 0603 TCR=100 AEC-Q200 |  | 0.55mm | KOA Speer | HV73V1JTTD103J |  | 660-HV73V1JTTD103J | https://www.mouser.co.uk/ProductDetail/KOA-Speer/HV73V1JTTD103J?qs=xZ%2FP%252Ba9zWqbXuiWLWua7%2Fw%3D%3D |  |  |  | 10k
R16 | 10k | HV73V1JTTD103J | CAPC1608X55N | Thick Film Resistors - SMD 10000Ohms 5% 0603 TCR=100 AEC-Q200 |  |  | Thick Film Resistors - SMD 10000Ohms 5% 0603 TCR=100 AEC-Q200 |  | 0.55mm | KOA Speer | HV73V1JTTD103J |  | 660-HV73V1JTTD103J | https://www.mouser.co.uk/ProductDetail/KOA-Speer/HV73V1JTTD103J?qs=xZ%2FP%252Ba9zWqbXuiWLWua7%2Fw%3D%3D |  |  |  | 10k
R17 | 0 Ohm | CR0603AJ_-000ELF | RESC1608X55N | Thick Film Resistors - SMD ResA 0603 0R Jumper 100mW AEC-Q200 |  |  | Thick Film Resistors - SMD ResA 0603 0R Jumper 100mW AEC-Q200 |  | 0.55mm | Bourns | CR0603AJ/-000ELF |  | 652-CR0603AJ/-000ELF | https://www.mouser.co.uk/ProductDetail/Bourns/CR0603AJ-000ELF/?qs=GedFDFLaBXF8EepoWODZMQ%3D%3D |  |  |  | 0 Ohm
R18 | 0 Ohm | CR0603AJ_-000ELF | RESC1608X55N | Thick Film Resistors - SMD ResA 0603 0R Jumper 100mW AEC-Q200 |  |  | Thick Film Resistors - SMD ResA 0603 0R Jumper 100mW AEC-Q200 |  | 0.55mm | Bourns | CR0603AJ/-000ELF |  | 652-CR0603AJ/-000ELF | https://www.mouser.co.uk/ProductDetail/Bourns/CR0603AJ-000ELF/?qs=GedFDFLaBXF8EepoWODZMQ%3D%3D |  |  |  | 0 Ohm
R19 | 15k | CRCW080515K0FKEBC | RESC2012X60N | Thick Film Resistors - SMD 1/8Watt 15Kohms 1% Commercial Use |  |  | Thick Film Resistors - SMD 1/8Watt 15Kohms 1% Commercial Use |  | 0.6mm | Vishay | CRCW080515K0FKEBC |  | 71-CRCW080515K0FKEBC | https://www.mouser.co.uk/ProductDetail/Vishay-Dale/CRCW080515K0FKEBC?qs=wd5RIQLrsJhoqkW23VWcpg%3D%3D |  |  |  | 15k
R20 | 576 | CRCW0805576RFKEA | RESC2012X50N | RES, THICK FILM, 576R, 1%, 0.125W, 0805 |  |  | 576 Ohms ±1% 0.125W, 1/8W Chip Resistor 0805 (2012 Metric) Automotive AEC-Q200 Thick Film | 541-576CCT-ND |  |  |  | Vishay |  |  | CRCW0805576RFKEA | 2012 Vishay | https://pricing.snapeda.com/search/part/CRCW0805576RFKEA/?ref=eda | 576
R24 | 0 Ohm | CR0603AJ_-000ELF | RESC1608X55N | Thick Film Resistors - SMD ResA 0603 0R Jumper 100mW AEC-Q200 |  |  | Thick Film Resistors - SMD ResA 0603 0R Jumper 100mW AEC-Q200 |  | 0.55mm | Bourns | CR0603AJ/-000ELF |  | 652-CR0603AJ/-000ELF | https://www.mouser.co.uk/ProductDetail/Bourns/CR0603AJ-000ELF/?qs=GedFDFLaBXF8EepoWODZMQ%3D%3D |  |  |  | 0 Ohm
R25 | 0 Ohm | CR0603AJ_-000ELF | RESC1608X55N | Thick Film Resistors - SMD ResA 0603 0R Jumper 100mW AEC-Q200 |  |  | Thick Film Resistors - SMD ResA 0603 0R Jumper 100mW AEC-Q200 |  | 0.55mm | Bourns | CR0603AJ/-000ELF |  | 652-CR0603AJ/-000ELF | https://www.mouser.co.uk/ProductDetail/Bourns/CR0603AJ-000ELF/?qs=GedFDFLaBXF8EepoWODZMQ%3D%3D |  |  |  | 0 Ohm
R26 | 0 Ohm | CR0603AJ_-000ELF | RESC1608X55N | Thick Film Resistors - SMD ResA 0603 0R Jumper 100mW AEC-Q200 |  |  | Thick Film Resistors - SMD ResA 0603 0R Jumper 100mW AEC-Q200 |  | 0.55mm | Bourns | CR0603AJ/-000ELF |  | 652-CR0603AJ/-000ELF | https://www.mouser.co.uk/ProductDetail/Bourns/CR0603AJ-000ELF/?qs=GedFDFLaBXF8EepoWODZMQ%3D%3D |  |  |  | 0 Ohm
R27 | 0 Ohm | CR0603AJ_-000ELF | RESC1608X55N | Thick Film Resistors - SMD ResA 0603 0R Jumper 100mW AEC-Q200 |  |  | Thick Film Resistors - SMD ResA 0603 0R Jumper 100mW AEC-Q200 |  | 0.55mm | Bourns | CR0603AJ/-000ELF |  | 652-CR0603AJ/-000ELF | https://www.mouser.co.uk/ProductDetail/Bourns/CR0603AJ-000ELF/?qs=GedFDFLaBXF8EepoWODZMQ%3D%3D |  |  |  | 0 Ohm
S1 | 1571294-3 | 1571294-3 | 15712943 | SWITCH,TACT,SMT,SEALED |  |  | SWITCH,TACT,SMT,SEALED |  | 5.5mm | TE Connectivity | 1571294-3 |  | 506-1571294-3 | https://www.mouser.co.uk/ProductDetail/TE-Connectivity-PB/1571294-3/?qs=bkeGI61iuy0TyJA2A0%2FQXg%3D%3D
S2 | 1571294-3 | 1571294-3 | 15712943 | SWITCH,TACT,SMT,SEALED |  |  | SWITCH,TACT,SMT,SEALED |  | 5.5mm | TE Connectivity | 1571294-3 |  | 506-1571294-3 | https://www.mouser.co.uk/ProductDetail/TE-Connectivity-PB/1571294-3/?qs=bkeGI61iuy0TyJA2A0%2FQXg%3D%3D
S3 | AS11CH | AS11CH | AS11CH | Switch Slide ON None OFF SPST Side Slide 0.1A 28VAC 28VDC 0.4VA 50000Cycles PC Pins Bracket Mount/Through Hole |  |  | Switch Slide ON None OFF SPST Side Slide 0.1A 28VAC 28VDC 0.4VA 50000Cycles PC Pins Bracket Mount/Through Hole |  | 6.18mm | NKK Switches | AS11CH |  | 633-AS11CH | https://www.mouser.co.uk/ProductDetail/NKK-Switches/AS11CH?qs=MODAV37v1mC%2FcDng1K%2FMsg%3D%3D
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

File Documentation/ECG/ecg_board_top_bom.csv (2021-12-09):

Comment | Designator | Footprint | LCSC Part #
0 Ohm | R1 R2 R35 R36 R37 | RESC1608X55N
0.1uF | C2 C3 C4 C5 C8 C10 C12 C13 C14 | CAPC2012X88N
1M | R26 | RESC1608X55N
1uF | C15 C16 C17 C18 | CAPC2012X100N
2.2nF | C26 C27 C28 C29 | CAPC2012X100N
2k | R7 R9 | RESC1608X55N
4.7uF | C9 C22 C23 | CAPC2114X145N
10M | R27 R28 R29 R30 | RESC1608X55N
10k | R3 R4 R5 R6 R15 R16 R17 | CAPC1608X55N
10uF | C19 | CAPC2012X135N
15k | R18 | RESC2012X60N
22.1K | R10 | RESC1005X40N
22uF | C7 C11 | CAPPC1609X90N
40.2k | R33 R34 | RESC3216X70N
47.5K | R8 | RESC1608X55N
47nF | C21 C24 | CAPC2012X140N
47pF | C20 | CAPC2012X95N
65ohm | R13 R14 | RESC2012X64N
100k | R11 R12 R31 R32 | RESC1608X50N
576 | R19 | RESC2012X50N
47346-1001 | J1 | 473461001
150141RV73100 | LED1 | SMD3528_1
1571294-3 | S1 S2 | 15712943
ADS1292RIPBSR | IC4 | QFP50P700X700X120-32N
AP2112K-3.3TRG1 | IC2 | SOT95P282X130-5N
BAT760-7 | D4 | SOD2513X120N
BSH205G2R | Q3 | SOT95P230X110-3N
CP2102N-A02-GQFN28 | IC3 | QFN50P500X500X80-29N
CPDQ5V0-HF | D1 D2 D3 | SODFL1006X40N
ESP32-WROOM-32D_M113DH2800PH3Q | ESP32 | ESP32WROOM32DM113DH2800PH3Q0
LTST-C193KRKT-5A | LED2 | LEDC1608X45N
MCP73832T-2DFI_OT | IC5 | SOT95P270X145-5N
SJ-3524-SMT-TR-GR | J3 | SJ3524SMTTRGR
SS34 | D5 | DIOM8059X256N
SS8050-G | Q1 Q2 | SOT95P240X115-3N

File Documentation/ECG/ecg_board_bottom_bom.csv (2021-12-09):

Comment | Designator | Footprint | LCSC Part #
0.1uF | C1 | CAPC2012X88N
22uF | C6 | CAPPC1609X90N

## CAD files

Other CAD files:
PCB enclousure/ECG PCB.ipt
PCB enclousure/ECG_cover.ipt
PCB enclousure/SD2104_case_design2.ipt
PCB enclousure/SPO2_cover.ipt
PCB enclousure/Spo2 PCB.ipt

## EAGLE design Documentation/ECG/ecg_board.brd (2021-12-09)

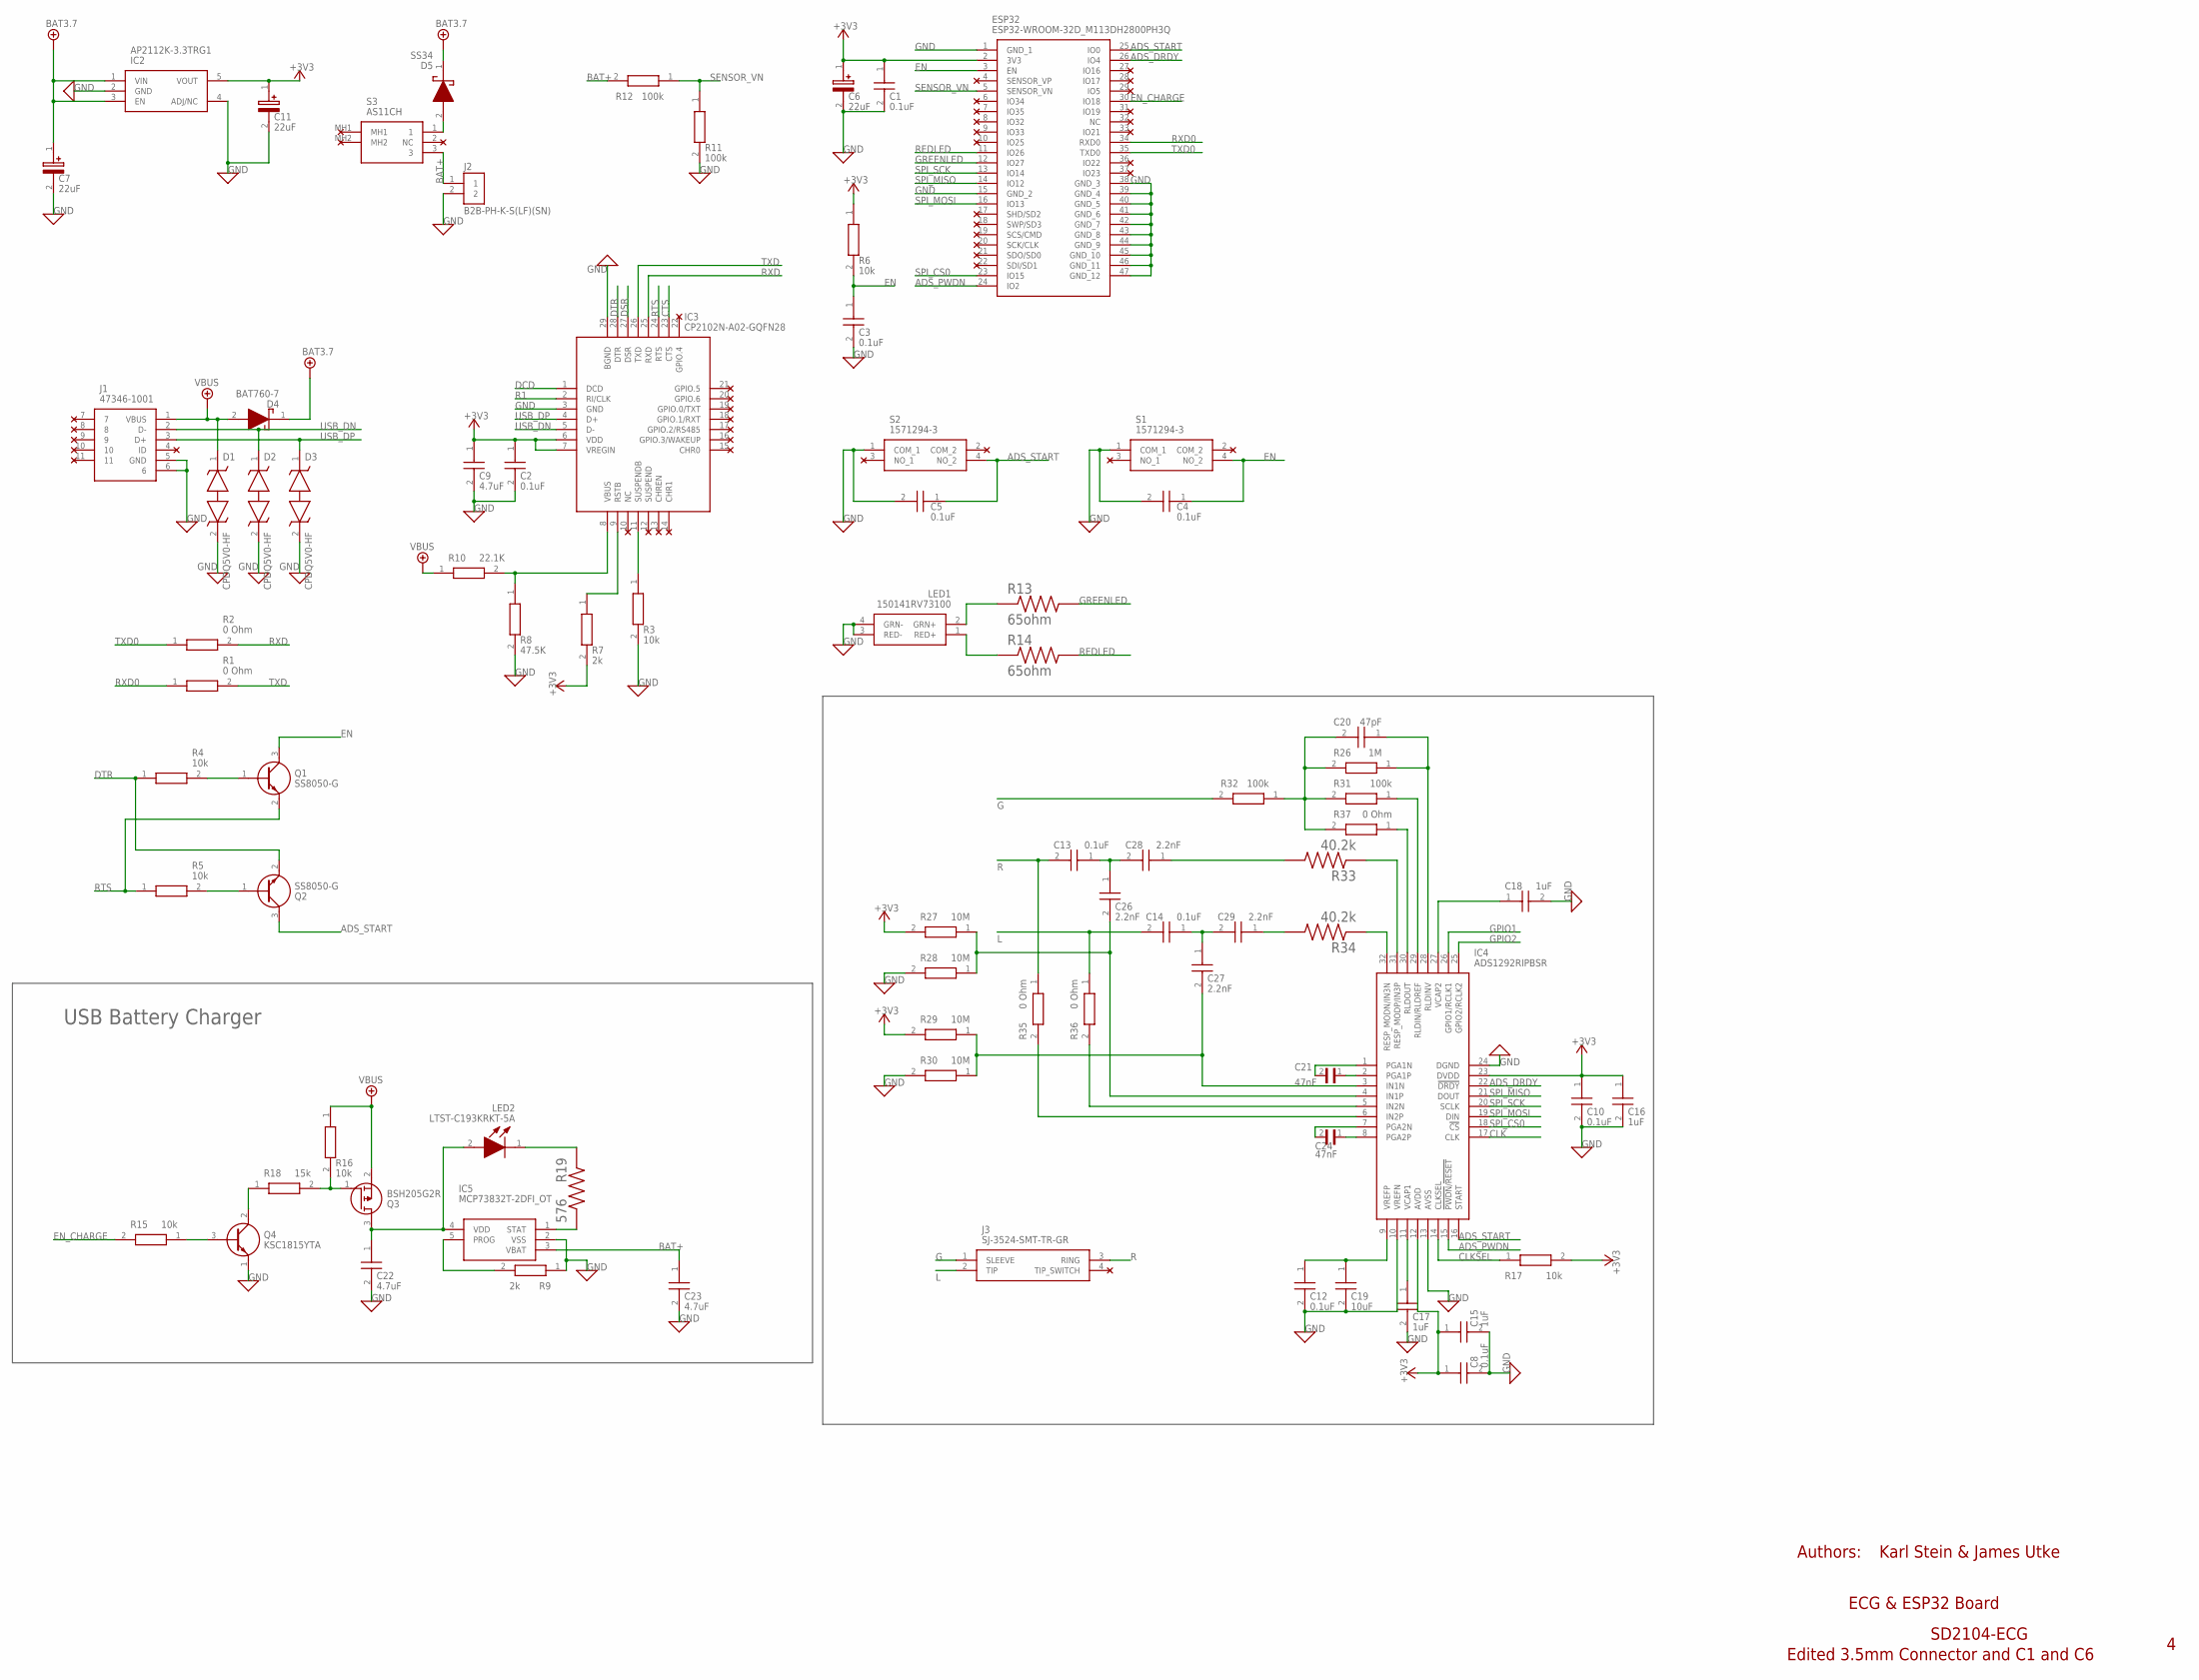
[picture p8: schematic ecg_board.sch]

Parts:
C1, C2, C3, C4, C5, C8, C10, C12, C13, C14: 0.1uF; CAPC2012X88N
C6, C7, C11: 22uF; CAPPC1609X90N
C9, C22, C23: 4.7uF; CAPC2114X145N
C15, C16, C17, C18: 1uF; CAPC2012X100N
C19: 10uF; CAPC2012X135N
C20: 47pF; CAPC2012X95N
C21, C24: 47nF; CAPC2012X140N
C26, C27, C28, C29: 2.2nF; CAPC2012X100N
D1, D2, D3: CPDQ5V0-HF; SODFL1006X40N
D4: BAT760-7; SOD2513X120N
D5: SS34; DIOM8059X256N
ESP32: ESP32-WROOM-32D_M113DH2800PH3Q; ESP32WROOM32DM113DH2800PH3Q0
IC2: AP2112K-3.3TRG1; SOT95P282X130-5N
IC3: CP2102N-A02-GQFN28; QFN50P500X500X80-29N
IC4: ADS1292RIPBSR; QFP50P700X700X120-32N
IC5: MCP73832T-2DFI_OT; SOT95P270X145-5N
J1: 47346-1001; 473461001
J2: B2B-PH-K-S(LF)(SN); JST_B2B-PH-K-S(LF)(SN)
J3: SJ-3524-SMT-TR-GR; SJ3524SMTTRGR
LED1: 150141RV73100; SMD3528_1
LED2: LTST-C193KRKT-5A; LEDC1608X45N
Q1, Q2: SS8050-G; SOT95P240X115-3N
Q3: BSH205G2R; SOT95P230X110-3N
Q4: KSC1815YTA; BC33740TA
R1, R2, R35, R36, R37: 0 Ohm; RESC1608X55N
R3, R4, R5, R6, R15, R16, R17: 10k; CAPC1608X55N
R7, R9: 2k; RESC1608X55N
R8: 47.5K; RESC1608X55N
R10: 22.1K; RESC1005X40N
R11, R12, R31, R32: 100k; RESC1608X50N
R13, R14: 65ohm; RESC2012X64N
R18: 15k; RESC2012X60N
R19: 576; RESC2012X50N
R26: 1M; RESC1608X55N
R27, R28, R29, R30: 10M; RESC1608X55N
R33, R34: 40.2k; RESC3216X70N
S1, S2: 1571294-3; 15712943
S3: AS11CH

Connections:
+3V3: C1.1, C2.1, C6.1 (+), C8.1, C9.1, C10.1, C11.1 (+), C15.1, C16.1, ESP32.2 (3V3), IC2.5 (VOUT), IC3.6 (VDD), IC3.7 (VREGIN), IC4.12 (AVDD), IC4.23 (DVDD), R6.1, R7.2, R17.2, R27.2, R29.2
+5V: C7.1 (+), D4.1 (K), D5.1 (K), IC2.1 (VIN), IC2.3 (EN)
+5V/1: D1.1, D4.2 (A), J1.1 (VBUS), Q3.2 (S), R10.1, R16.1
ADS_DRDY: ESP32.26 (IO4), IC4.22 (!DRDY)
ADS_PWDN: ESP32.24 (IO2), IC4.15 (!PWDN!/!RESET)
ADS_START: C5.1, ESP32.25 (IO0), IC4.16 (START), Q2.3 (C), S2.4 (NO_2)
BAT+: C23.1, IC5.3 (VBAT), J2.1, R12.2, S3.3
CLK: IC4.17 (CLK)
CLKSEL: IC4.14 (CLKSEL), R17.1
CTS: IC3.23 (CTS)
DCD: IC3.1 (DCD)
DSR: IC3.27 (DSR)
DTR: IC3.28 (DTR), Q2.2 (E), R4.1
EN: C3.1, C4.1, ESP32.3 (EN), Q1.3 (C), R6.2, S1.4 (NO_2)
EN_CHARGE: ESP32.30 (IO18), R15.2
G: J3.1 (SLEEVE), R32.2
GND: C1.2, C2.2, C3.2, C4.2, C5.2, C6.2 (-), C7.2 (-), C8.2, C9.2, C10.2, C11.2 (-), C12.2, C15.2, C16.2, C17.2, C18.2, C19.2, C22.2, C23.2, D1.2, D2.2, D3.2, ESP32.1 (GND_1), ESP32.15 (GND_2), ESP32.38 (GND_3), ESP32.39 (GND_4), ESP32.40 (GND_5), ESP32.41 (GND_6), ESP32.42 (GND_7), ESP32.43 (GND_8), ESP32.44 (GND_9), ESP32.45 (GND_10), ESP32.46 (GND_11), ESP32.47 (GND_12), IC2.2 (GND), IC2.4 (ADJ/NC), IC3.3 (GND), IC3.29 (BGND), IC4.10 (VREFN), IC4.13 (AVSS), IC4.24 (DGND), IC5.2 (VSS), J1.5 (GND), J1.6, J2.2, LED1.3 (RED-), LED1.4 (GRN-), Q4.1 (E), R3.2, R8.2, R9.1, R11.2, R28.2, R30.2, S1.1 (COM_1), S2.1 (COM_1)
GPIO1: IC4.26 (GPIO1/RCLK1)
GPIO2: IC4.25 (GPIO2/RCLK2)
GREENLED: ESP32.12 (IO27), R13.2
L: C14.2, J3.2 (TIP), R36.1
unnamed: LED1.2 (GRN+), R13.1
unnamed: LED1.1 (RED+), R14.1
unnamed: C12.1, C19.1, IC4.9 (VREFP)
unnamed: Q1.1 (B), R4.2
unnamed: Q2.1 (B), R5.2
unnamed: C17.1, IC4.11 (VCAP1)
unnamed: C18.1, IC4.27 (VCAP2)
unnamed: LED2.1 (K), R19.1
unnamed: IC4.32 (RESP_MODN/IN3N), R34.1
unnamed: D5.2 (A), S3.1
unnamed: IC5.5 (PROG), R9.2
unnamed: Q4.3 (B), R15.1
unnamed: IC4.31 (RESP_MODP/IN3P), R33.1
unnamed: Q4.2 (C), R18.1
unnamed: C29.1, R34.2
unnamed: IC3.11 (SUSPENDB), R3.1
unnamed: IC3.9 (RSTB), R7.1
unnamed: IC3.8 (VBUS), R8.1, R10.2
unnamed: C14.1, C27.1, C29.2
unnamed: C13.1, C26.1, C28.2
unnamed: C28.1, R33.2
unnamed: IC4.5 (IN2N), R36.2
unnamed: IC4.6 (IN2P), R35.2
unnamed: Q3.1 (G), R16.2, R18.2
unnamed: IC5.1 (STAT), R19.2
unnamed: C20.2, R26.2, R31.2, R32.1, R37.2
unnamed: C22.1, IC5.4 (VDD), LED2.2 (A), Q3.3 (D)
unnamed: C21.1, IC4.2 (PGA1P)
unnamed: C21.2, IC4.1 (PGA1N)
unnamed: C27.2, IC4.3 (IN1N), R29.1, R30.1
unnamed: C26.2, IC4.4 (IN1P), R27.1, R28.1
unnamed: C24.1, IC4.8 (PGA2P)
unnamed: C24.2, IC4.7 (PGA2N)
unnamed: IC4.29 (RLDIN/RLDREF), R31.1
unnamed: IC4.30 (RLDOUT), R37.1
unnamed: C20.1, IC4.28 (RLDINV), R26.1
R: C13.2, J3.3 (RING), R35.1
R1: IC3.2 (RI/CLK)
REDLED: ESP32.11 (IO26), R14.2
RTS: IC3.24 (RTS), Q1.2 (E), R5.1
RXD: IC3.25 (RXD), R2.2
RXD0: ESP32.34 (RXD0), R1.1
SENSOR_VN: ESP32.5 (SENSOR_VN), R11.1, R12.1
SPI_CS0: ESP32.23 (IO15), IC4.18 (!CS)
SPI_MISO: ESP32.14 (IO12), IC4.21 (DOUT)
SPI_MOSI: ESP32.16 (IO13), IC4.19 (DIN)
SPI_SCK: ESP32.13 (IO14), IC4.20 (SCLK)
TXD: IC3.26 (TXD), R1.2
TXD0: ESP32.35 (TXD0), R2.1
USB_DN: D2.1, IC3.5 (D-), J1.2 (D-)
USB_DP: D3.1, IC3.4 (D+), J1.3 (D+)

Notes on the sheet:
ECG & ESP32 Board
Authors:
Karl Stein & James Utke
SD2104-ECG
USB Battery Charger
Edited 3.5mm Connector and C1 and C6

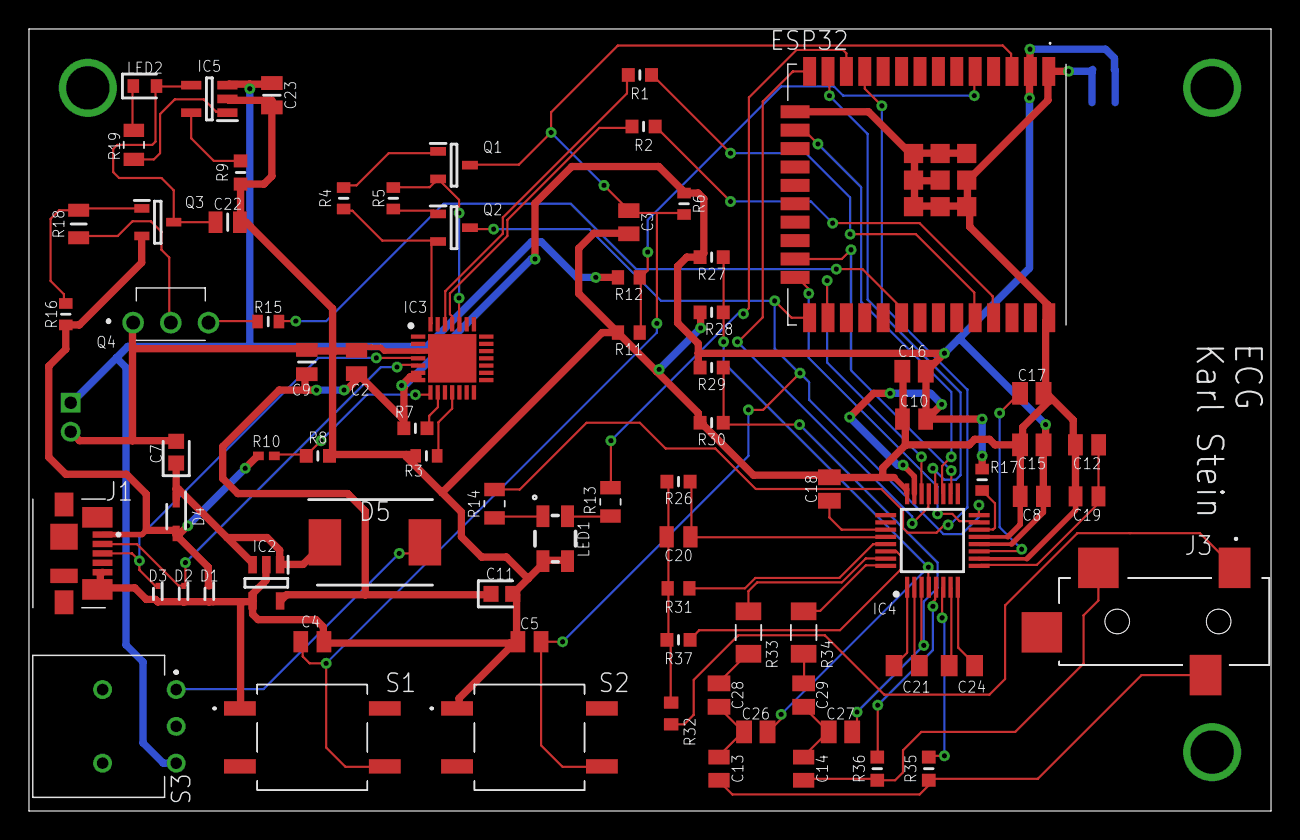
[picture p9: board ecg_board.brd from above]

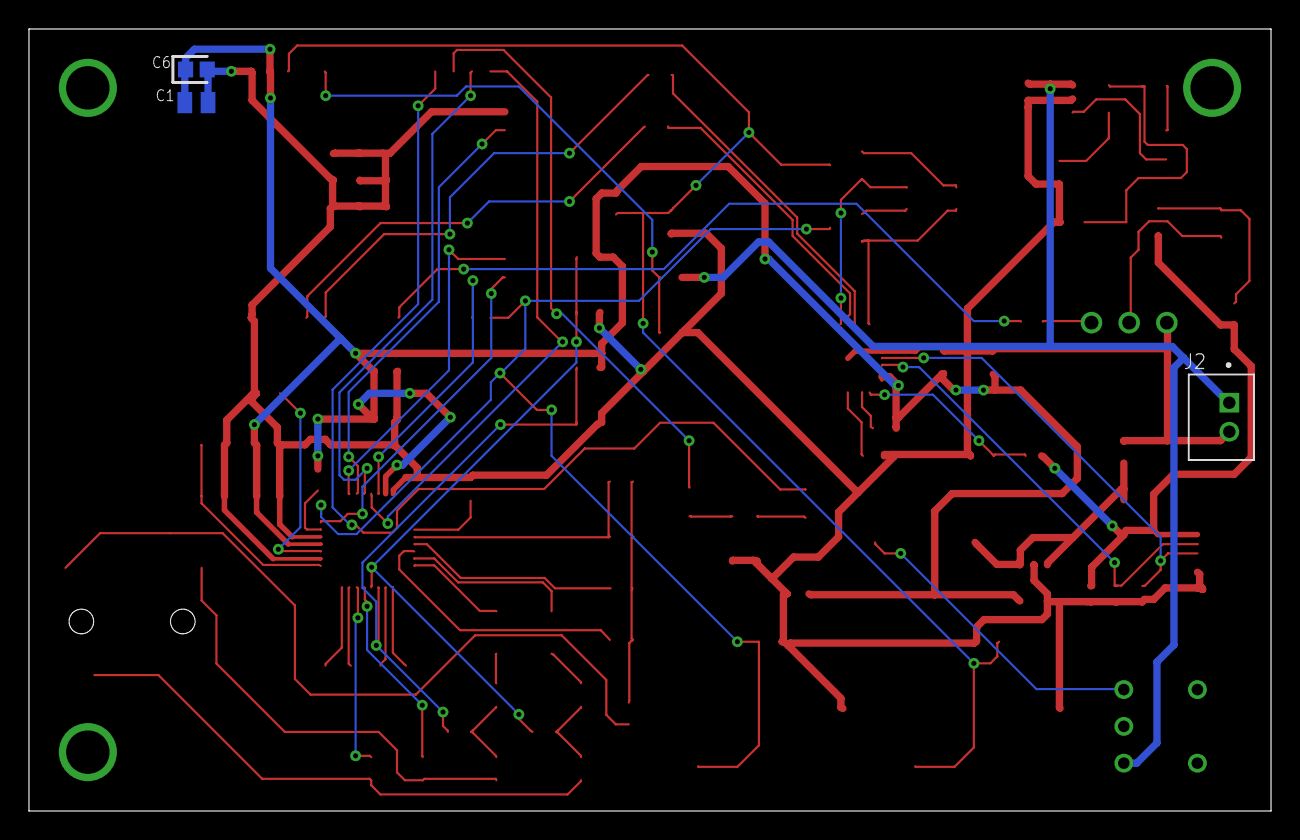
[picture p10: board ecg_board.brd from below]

Board: 2 copper layers, 85.7 x 54.0 mm, 81 parts (3 on the bottom side), 65 nets.

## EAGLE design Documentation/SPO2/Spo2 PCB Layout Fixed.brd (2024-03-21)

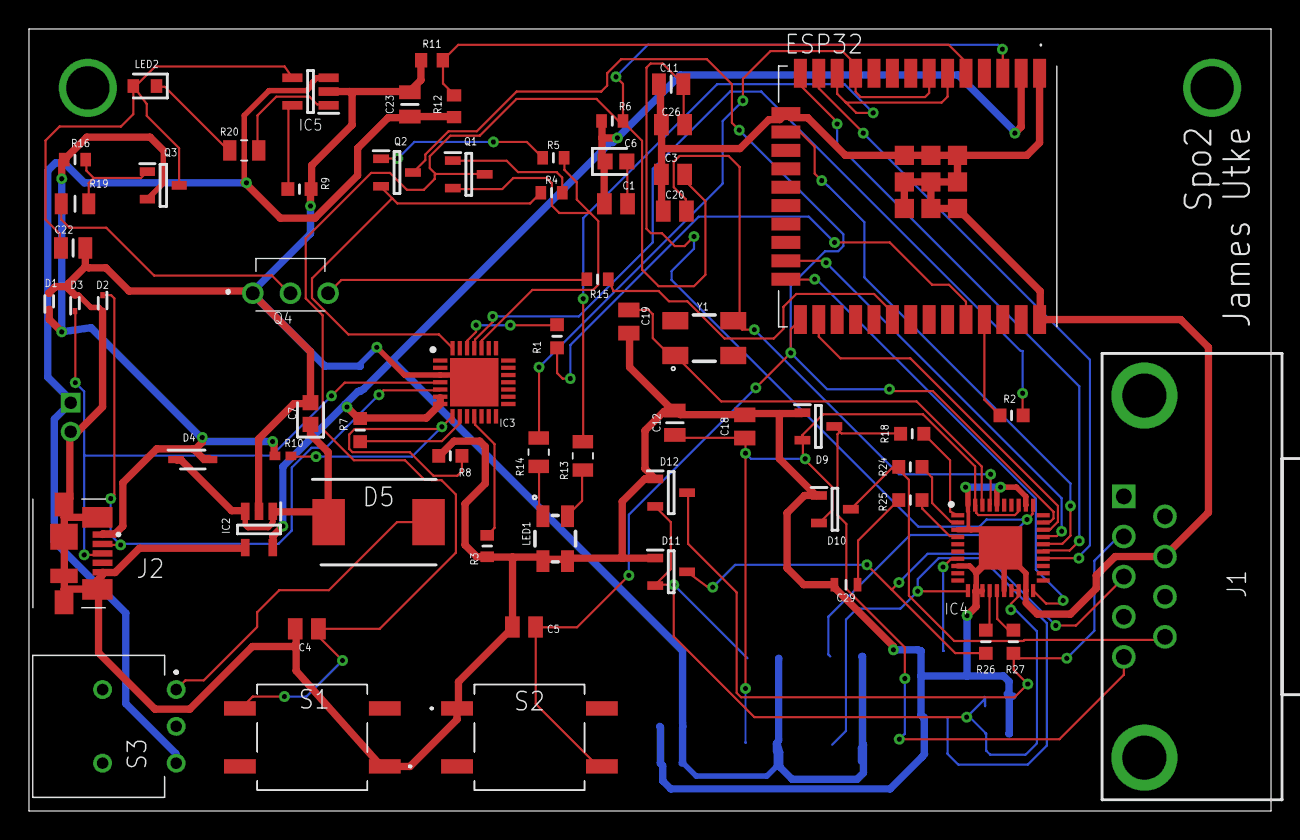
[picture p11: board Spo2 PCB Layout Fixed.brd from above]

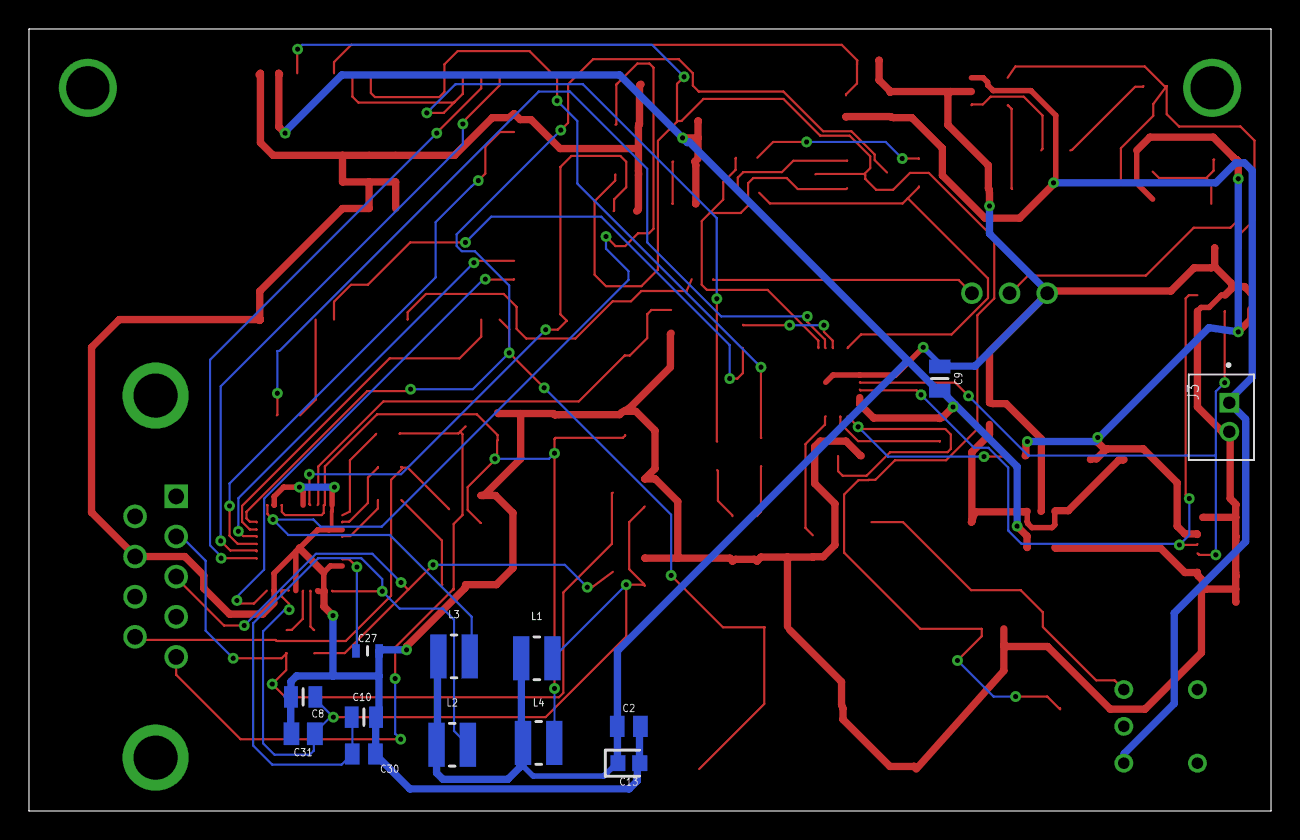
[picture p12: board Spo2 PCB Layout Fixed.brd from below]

Board: 2 copper layers, 85.7 x 54.0 mm, 77 parts (13 on the bottom side), 58 nets.

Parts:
C1, C2, C3, C4, C5, C18, C26, C30: 0.1uF; CAPC2012X88N
C6, C7, C13: 22uF; CAPPC1609X90N
C8, C10, C11, C12: 10uF; CAPC2114X145N@1
C9, C22, C23: 4.7uF; CAPC2114X145N
C19, C20: 22pF; CAPC2012X88N@1
C27, C29: 2.2uF; CAPC1608X80N
C31: 1uF; CAPC2012X100N
D1, D2, D3: CPDQ5V0-HF; SODFL1006X40N
D4: BAT760-7; SOD2513X120N
D5: SS34; DIOM8059X256N
D9, D10, D11, D12: BAT54S; SOT95P240X110-3N
ESP32: ESP32-WROOM-32D_M113DH2800PH3Q; ESP32WROOM32DM113DH2800PH3Q0
IC2: AP2112K-3.3TRG1; SOT95P282X130-5N
IC3: CP2102N-A02-GQFN28; QFN50P500X500X80-29N
IC4: AFE4400RHAR; QFN50P600X600X100-41N
IC5: MCP73832T-2DFI_OT; SOT95P270X145-5N
J1: 182-009-213R161; 182009213R161
J2: 47346-1001; 473461001
J3: B2B-PH-K-S(LF)(SN); JST_B2B-PH-K-S(LF)(SN)
L1, L2, L3, L4: 470nH; LPS3010471MRC
LED1: 150141RV73100; SMD3528_1
LED2: LTST-C193KRKT-5A; LEDC1608X45N
Q1, Q2: SS8050-G; SOT95P240X115-3N
Q3: BSH205G2R; SOT95P230X110-3N
Q4: KSC1815YTA; BC33740TA
R1, R2, R18, R24, R25, R26, R27: 0 Ohm; RESC1608X55N
R3, R4, R5, R6, R15, R16: 10k; CAPC1608X55N
R7, R9: 2k; RESC1608X55N
R8: 47.5K; RESC1608X55N
R10: 22.1K; RESC1005X40N
R11, R12: 100k; RESC1608X50N
R13, R14: 65ohm; RESC2012X64N
R19: 15k; RESC2012X60N
R20: 576; RESC2012X50N
S1, S2: 1571294-3; 15712943
S3: AS11CH
Y1: ABM3B-8.000MHZ-10-1-U-T; ABM3B

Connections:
0: C1.2, C6.2
!ADC_RESET: C5.1, ESP32.25, IC4.29, Q2.3, S2.4
!AFE_PDN: ESP32.24, IC4.20
+3V3: C1.1, C2.1, C6.1, C9.1, C13.1, ESP32.2, IC2.5, IC3.6, IC3.7, L1.1, L2.1, L3.1, L4.1, R6.1, R7.2
+5V: C7.1, D4.1, D5.1, IC2.1, IC2.3
+5V/1: D1.1, D4.2, J2.1, Q3.2, R10.1, R16.1
ADC_RDY: ESP32.26, IC4.28
BAT+: C23.1, IC5.3, J3.1, R12.2, S3.3
DTR: IC3.28, Q2.2, R4.1
EN: C3.1, C4.1, ESP32.3, Q1.3, R6.2, S1.4
EN_CHARGE: ESP32.30, R15.2
GND: C2.2, C3.2, C4.2, C5.2, C7.2, C8.2, C9.2, C10.2, C11.2, C12.2, C13.2, C18.2, C19.2, C20.2, C22.2, C23.2, C26.2, C27.2, C29.2, C30.2, C31.2, D1.2, D2.2, D3.2, D9.1, D10.1, D11.1, D12.1, ESP32.1, ESP32.15, ESP32.38, ESP32.39, ESP32.40, ESP32.41, ESP32.42, ESP32.43, ESP32.44, ESP32.45, ESP32.46, ESP32.47, IC2.2, IC2.4, IC3.3, IC3.29, IC4.3, IC4.8, IC4.12, IC4.13, IC4.16, IC4.19, IC4.32, IC4.36, IC4.40, IC4.41, IC5.2, J1.7, J2.5, J2.6, J2.7, J2.8, J2.9, J2.10, J2.11, J3.2, LED1.3, LED1.4, Q4.1, R3.2, R8.2, R9.1, R11.2, S1.1, S2.1
GREENLED: ESP32.6, ESP32.12, R13.2
INN: D9.3, J1.5, R18.2
INP: D10.3, J1.9, R24.2
LED_DRV_SUP: C8.1, C31.1, D11.2, D12.2, IC4.17, IC4.18, L1.2
unnamed: LED1.2, R13.1
unnamed: LED1.1, R14.1
unnamed: C19.1, IC4.38, Y1.1
unnamed: Q1.1, R4.2
unnamed: Q2.1, R5.2
unnamed: IC5.5, R9.2
unnamed: C20.1, IC4.37, Y1.3
unnamed: C27.1, IC4.7
unnamed: IC4.1, R18.1
unnamed: IC4.2, R24.1
unnamed: IC4.14, R26.1
unnamed: C29.1, R25.2
unnamed: IC4.15, R27.1
unnamed: Q4.3, R15.1
unnamed: Q4.2, R19.1
unnamed: IC3.11, R3.1
unnamed: IC3.9, R7.1
unnamed: IC3.8, R8.1, R10.2
unnamed: LED2.1, R20.1
unnamed: D5.2, S3.1
unnamed: Q3.1, R16.2, R19.2
unnamed: IC5.1, R20.2
unnamed: C22.1, IC5.4, LED2.2, Q3.3
REDLED: ESP32.7, ESP32.11, R14.2
RTS: IC3.24, Q1.2, R5.1
RXD: IC3.25, R2.2
RXD0: ESP32.34, R1.1
RX_ANA_SUP: C12.1, C18.1, D9.2, D10.2, IC4.33, IC4.39, L4.2
RX_DIG_SUP: C11.1, C26.1, IC4.31, L3.2
SENSOR_VN: ESP32.5, R11.1, R12.1
SPI_CS0: ESP32.23, IC4.27
SPI_MISO: ESP32.14, IC4.25
SPI_MOSI: ESP32.16, IC4.26
SPI_SCK: ESP32.13, IC4.24
TXD: IC3.26, R1.2
TXD0: ESP32.35, R2.1
TXN: D11.3, J1.3, R26.2
TXP: D12.3, J1.2, R27.2
TX_CTRL_SUP: C10.1, C30.1, IC4.11, L2.2
USB_DN: D2.1, IC3.5, J2.2
USB_DP: D3.1, IC3.4, J2.3
VCM: IC4.4, R25.1

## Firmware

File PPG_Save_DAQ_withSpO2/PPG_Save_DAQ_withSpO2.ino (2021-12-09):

//////////////////////////////////////////////////////////////////////////////////////////
//
//   AFE44xx Arduino Firmware
//
//   Copyright (c) 2016 ProtoCentral
//
//   SpO2 computation based on original code from Maxim Integrated
//
//   This software is licensed under the MIT License(http://opensource.org/licenses/MIT).
//
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
//   For information on how to use the HealthyPi, visit https://github.com/Protocentral/afe44xx_Oximeter
/////////////////////////////////////////////////////////////////////////////////////////

#include <string.h>
#include <SPI.h>
#include <math.h>
#include <stdio.h>

#include <WiFi.h>
#include <WebServer.h>
#include <time.h>
#include <AutoConnect.h>
#include <NTPClient.h>
#include <WiFiUdp.h>
#include <ThingsBoard.h>


//wifi and device on Thingsboard
//#define WIFI_AP "NDSU IoT"
//#define WIFI_PASSWORD "bacondotwager"
#define TOKEN "AlfXtRanSlldLQG2tZNz"
char thingsboardServer[] = "134.129.122.213";
WiFiClient wifiClient;
ThingsBoard tb(wifiClient);
int status = WL_IDLE_STATUS;
unsigned long lastSend;

//Autoconnect Wifi
WebServer Server;
AutoConnect Portal(Server);
AutoConnectConfig Config;

//NTP library to get real time from server
#define NTP_OFFSET   0 * 60      // In seconds
#define NTP_INTERVAL 5 * 1000    // In miliseconds
#define NTP_ADDRESS  "pool.ntp.org"
WiFiUDP ntpUDP;
NTPClient timeClient(ntpUDP, NTP_ADDRESS, NTP_OFFSET, NTP_INTERVAL);

//LED Time Variables
unsigned long current_time_LED;
unsigned long previous_time_LED;
unsigned long elapsed_time_LED = 0;
float voltage = 0.0f;
float percentage = 0.0f;
int battStatus = 5; //Start in default mode (not transmitting)
int ledState = LOW;   // ledState used to set the LED

//afe44xx Register definition
#define CONTROL0    0x00
#define LED2STC     0x01
#define LED2ENDC    0x02
#define LED2LEDSTC    0x03
#define LED2LEDENDC   0x04
#define ALED2STC    0x05
#define ALED2ENDC   0x06
#define LED1STC     0x07
#define LED1ENDC    0x08
#define LED1LEDSTC    0x09
#define LED1LEDENDC   0x0a
#define ALED1STC    0x0b
#define ALED1ENDC   0x0c
#define LED2CONVST    0x0d
#define LED2CONVEND   0x0e
#define ALED2CONVST   0x0f
#define ALED2CONVEND  0x10
#define LED1CONVST    0x11
#define LED1CONVEND   0x12
#define ALED1CONVST   0x13
#define ALED1CONVEND  0x14
#define ADCRSTCNT0    0x15
#define ADCRSTENDCT0  0x16
#define ADCRSTCNT1    0x17
#define ADCRSTENDCT1  0x18
#define ADCRSTCNT2    0x19
#define ADCRSTENDCT2  0x1a
#define ADCRSTCNT3    0x1b
#define ADCRSTENDCT3  0x1c
#define PRPCOUNT    0x1d
#define CONTROL1    0x1e
#define SPARE1      0x1f
#define TIAGAIN     0x20
#define TIA_AMB_GAIN  0x21
#define LEDCNTRL    0x22
#define CONTROL2    0x23
#define SPARE2      0x24
#define SPARE3      0x25
#define SPARE4      0x26
#define SPARE4      0x26
#define RESERVED1   0x27
#define RESERVED2   0x28
#define ALARM     0x29
#define LED2VAL     0x2a
#define ALED2VAL    0x2b
#define LED1VAL     0x2c
#define ALED1VAL    0x2d
#define LED2ABSVAL    0x2e
#define LED1ABSVAL    0x2f
#define DIAG      0x30
#define count 60

#define CES_CMDIF_PKT_START_1   0x0A
#define CES_CMDIF_PKT_START_2   0xFA
#define CES_CMDIF_TYPE_DATA   0x02
#define CES_CMDIF_PKT_STOP    0x0B


//int IRheartsignal[count];
//int Redheartsignal[count];
int IRdc[count];
int Reddc[count];
double difIRheartsig_dc;
double difREDheartsig_dc;
double powdifIR;
double powdifRed;
double IRac;
double Redac;
double SpOpercentage;
double Ratio;
unsigned long start_time;
unsigned long end_time;

//Pin declarations
const int SPISTE = 15;  // chip select - IO15
const int SPIDRDY = 4;  // data ready pin - IO4
volatile int drdy_trigger = LOW;
const int RESET = 0; // reset pin - IO0
const int PWDN = 2; // powerdown pin - IO2
#define GRN_LED 27          //TBD after soldering
#define RED_LED 26          //TBD after soldering
#define BATTERY_IN 39
#define CHARGER 18

void afe44xxInit (void);
void afe44xxWrite (uint8_t address, uint32_t data);
unsigned long afe44xxRead (uint8_t address);
signed long average_BPM( signed long );
volatile char DataPacketHeader[6];
volatile char DataPacket[10];
volatile char DataPacketFooter[2];
int datalen = 0x09;
//long unsigned int time;

volatile static int SPI_RX_Buff_Count = 0;
volatile char *SPI_RX_Buff_Ptr;
volatile int afe44xx_data_ready = false;
volatile unsigned int pckt = 0, buff = 0, t = 0;
unsigned long ueegtemp = 0, ueegtemp2 = 0;
unsigned long IRtemp, REDtemp;
signed long seegtemp = 0, seegtemp2 = 0;
volatile int i;


uint16_t aun_ir_buffer[100]; //infrared LED sensor data
uint16_t aun_red_buffer[100];  //red LED sensor data

#define FS            25    //sampling frequency
#define BUFFER_SIZE  (FS*4)
#define MA4_SIZE  4 // DONOT CHANGE
#define min(x,y) ((x) < (y) ? (x) : (y))

const uint8_t uch_spo2_table[184] = { 95, 95, 95, 96, 96, 96, 97, 97, 97, 97, 97, 98, 98, 98, 98, 98, 99, 99, 99, 99,
                                      99, 99, 99, 99, 100, 100, 100, 100, 100, 100, 100, 100, 100, 100, 100, 100, 100, 100, 100, 100,
                                      100, 100, 100, 100, 99, 99, 99, 99, 99, 99, 99, 99, 98, 98, 98, 98, 98, 98, 97, 97,
                                      97, 97, 96, 96, 96, 96, 95, 95, 95, 94, 94, 94, 93, 93, 93, 92, 92, 92, 91, 91,
                                      90, 90, 89, 89, 89, 88, 88, 87, 87, 86, 86, 85, 85, 84, 84, 83, 82, 82, 81, 81,
                                      80, 80, 79, 78, 78, 77, 76, 76, 75, 74, 74, 73, 72, 72, 71, 70, 69, 69, 68, 67,
                                      66, 66, 65, 64, 63, 62, 62, 61, 60, 59, 58, 57, 56, 56, 55, 54, 53, 52, 51, 50,
                                      49, 48, 47, 46, 45, 44, 43, 42, 41, 40, 39, 38, 37, 36, 35, 34, 33, 31, 30, 29,
                                      28, 27, 26, 25, 23, 22, 21, 20, 19, 17, 16, 15, 14, 12, 11, 10, 9, 7, 6, 5,
                                      3, 2, 1
                                    } ;

static  int32_t an_x[ BUFFER_SIZE];
static  int32_t an_y[ BUFFER_SIZE];

volatile int8_t n_buffer_count; //data length

int32_t n_spo2;  //SPO2 value
int8_t ch_spo2_valid;  //indicator to show if the SPO2 calculation is valid
int32_t n_heart_rate; //heart rate value
int8_t  ch_hr_valid;  //indicator to show if the heart rate calculation is valid

long status_byte = 0;
uint8_t LeadStatus = 0;
boolean leadoff_deteted = true;
uint8_t spo2_probe_open = false;
int dec = 0;

//timestamp variables
unsigned long long timestamp;
unsigned long long real_time;
unsigned long long previous_ts;
int ii = 0;

void rootPage(){
  char content[] = "ESP32 Autoconnect Setup";
  Server.send(200, "text/plain", content);
}

void setup()
{
  Serial.begin(115200);
    // Serial.begin(57600);
  //Serial.begin(9600);
  //InitWiFi();
  //LED and battery read pins
  pinMode(GRN_LED, OUTPUT);
  pinMode(RED_LED, OUTPUT);
  pinMode(BATTERY_IN, INPUT);
  pinMode(CHARGER,OUTPUT);
  digitalWrite(RED_LED, HIGH);
  // Enable saved past credential by autoReconnect option,
  // even once it is disconnected.
  Config.apid = "SpO2ap";
  Config.apip =  IPAddress(192,168,10,101);
  Config.autoReconnect = false;
  Config.retainPortal = true;
  Config.autoRise = true;
  //Config.preserveAPMode = true;
  Config.immediateStart = true;
  Config.hostName = "esp32-01";
  Portal.config(Config);
  Server.on("/", rootPage);
  // Establish a connection with an autoReconnect option.
  if (Portal.begin()) {
    Serial.println("WiFi connected: " + WiFi.localIP().toString());
    Serial.println(WiFi.getHostname());
  }
  timeClient.begin();
  timeClient.update();
  timestamp = timeClient.getEpochTime();

  //set up for data saving
  Serial.println("CLEARDATA");
  Serial.println("LABEL,Date,Time,Timestamp,PPG_IR,PPG_Red");
  Serial.println("RESETTIMER");
  
  
  Serial.println("Intilazition AFE44xx.. ");
  delay(2000) ;   // pause for a moment

  analogReadResolution(12);
  //SPI.begin();
  SPI.begin(14,12,13,15);

  // set the directions
  pinMode (RESET, OUTPUT); //Slave Select
  pinMode (PWDN, OUTPUT); //Slave Select

  digitalWrite(RESET, LOW);
  delay(500);
  digitalWrite(RESET, HIGH);
  delay(500);
  digitalWrite(PWDN, LOW);
  delay(500);
  digitalWrite(PWDN, HIGH);
  delay(500);
  pinMode (SPISTE, OUTPUT); //Slave Select
  pinMode (SPIDRDY, INPUT); // data ready
  //  Serial.println(SPISTE);
  //  Serial.println(SS);
  //  Serial.println(digitalRead(SPISTE));
  //  Serial.println(digitalRead(SCK));
  //  Serial.println(digitalRead(MOSI));

  attachInterrupt(SPIDRDY, afe44xx_drdy_event, FALLING); // Digital2 is attached to Data ready pin of AFE is interrupt0 in ARduino
  //   attachInterrupt(0, afe44xx_drdy_event, RISING );
  // set SPI transmission
  SPI.setClockDivider (SPI_CLOCK_DIV8); // set Speed as 2MHz , 16MHz/ClockDiv
  //SPI.setDataMode (SPI_MODE0);          //Set SPI mode as 0
  SPI.setDataMode (SPI_MODE1);          //Set SPI mode as 1
  SPI.setBitOrder (MSBFIRST);           //MSB first

  // Packet structure
  DataPacketHeader[0] = CES_CMDIF_PKT_START_1;  //packet header1 0x0A
  DataPacketHeader[1] = CES_CMDIF_PKT_START_2;  //packet header2 0xFA
  DataPacketHeader[2] = datalen;                // data length 9
  DataPacketHeader[3] = (uint8_t)(datalen >> 8);
  DataPacketHeader[4] = CES_CMDIF_TYPE_DATA;

  DataPacketFooter[0] = 0x00;
  DataPacketFooter[1] = CES_CMDIF_PKT_STOP;
  afe44xxInit ();
  Serial.println("initialization is done");
}
/////////////////////////////////////////////////////////////////////////////////////////////////////////////////
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

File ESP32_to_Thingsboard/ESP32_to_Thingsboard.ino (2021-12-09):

//////////////////////////////////////////////////////////////////////////////////////////
//
//   Arduino Library for ADS1292R Shield/Breakout
//
//   Copyright (c) 2017 ProtoCentral
//   Heartrate and respiration computation based on original code from Texas Instruments
//
//   This software is licensed under the MIT License(http://opensource.org/licenses/MIT).
//
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
//   Requires g4p_control graphing library for processing.  Built on V4.1
//   Downloaded from Processing IDE Sketch->Import Library->Add Library->G4P Install

// If you have bought the breakout the connection with the Arduino board is as follows:
//
//|ads1292r pin label| Arduino Connection   |Pin Function      |
//|----------------- |:--------------------:|-----------------:|
//| VDD              | +5V                  |  Supply voltage  |
//| PWDN/RESET       | D4                   |  Reset           |
//| START            | D5                   |  Start Input     |
//| DRDY             | D6                   |  Data Ready Outpt|
//| CS               | D7                   |  Chip Select     |
//| MOSI             | D11                  |  Slave In        |
//| MISO             | D12                  |  Slave Out       |
//| SCK              | D13                  |  Serial Clock    |
//| GND              | Gnd                  |  Gnd             |
//
/////////////////////////////////////////////////////////////////////////////////////////

#include <ads1292r.h>
#include <string.h>
#include <SPI.h>
#include <math.h>
#include <stdio.h>

#include <WiFi.h>
#include <WebServer.h>
#include <time.h>
#include <AutoConnect.h>
#include <NTPClient.h>
#include <WiFiUdp.h>
#include <ThingsBoard.h>

ads1292r ADS1292;   // define class

//Autoconnect
static const char AUX_TIMEZONE[] PROGMEM = R"(
{
  "title": "TimeZone",
  "uri": "/timezone",
  "menu": true,
  "element": [
    {
      "name": "caption",
      "type": "ACText",
      "value": "Sets the time zone to get the current local time.",
      "style": "font-family:Arial;font-weight:bold;text-align:center;margin-bottom:10px;color:DarkSlateBlue"
    },
    {
      "name": "timezone",
      "type": "ACSelect",
      "label": "Select TZ name",
      "option": [],
      "selected": 10
    },
    {
      "name": "newline",
      "type": "ACElement",
      "value": "<br>"
    },
    {
      "name": "start",
      "type": "ACSubmit",
      "value": "OK",
      "uri": "/start"
    }
  ]
}
)";

typedef struct {
  const char* zone;
  const char* ntpServer;
  int8_t      tzoff;
} Timezone_t;

static const Timezone_t TZ[] = {
  { "Europe/London", "europe.pool.ntp.org", 0 },
  { "Europe/Berlin", "europe.pool.ntp.org", 1 },
  { "Europe/Helsinki", "europe.pool.ntp.org", 2 },
  { "Europe/Moscow", "europe.pool.ntp.org", 3 },
  { "Asia/Dubai", "asia.pool.ntp.org", 4 },
  { "Asia/Karachi", "asia.pool.ntp.org", 5 },
  { "Asia/Dhaka", "asia.pool.ntp.org", 6 },
  { "Asia/Jakarta", "asia.pool.ntp.org", 7 },
  { "Asia/Manila", "asia.pool.ntp.org", 8 },
  { "Asia/Tokyo", "asia.pool.ntp.org", 9 },
  { "Australia/Brisbane", "oceania.pool.ntp.org", 10 },
  { "Pacific/Noumea", "oceania.pool.ntp.org", 11 },
  { "Pacific/Auckland", "oceania.pool.ntp.org", 12 },
  { "Atlantic/Azores", "europe.pool.ntp.org", -1 },
  { "America/Noronha", "south-america.pool.ntp.org", -2 },
  { "America/Araguaina", "south-america.pool.ntp.org", -3 },
  { "America/Blanc-Sablon", "north-america.pool.ntp.org", -4},
  { "America/New_York", "north-america.pool.ntp.org", -5 },
  { "America/Chicago", "north-america.pool.ntp.org", -6 },
  { "America/Denver", "north-america.pool.ntp.org", -7 },
  { "America/Los_Angeles", "north-america.pool.ntp.org", -8 },
  { "America/Anchorage", "north-america.pool.ntp.org", -9 },
  { "Pacific/Honolulu", "north-america.pool.ntp.org", -10 },
  { "Pacific/Samoa", "oceania.pool.ntp.org", -11 }
};

WebServer Server;
AutoConnect       Portal(Server);
AutoConnectConfig Config;       // Enable autoReconnect supported on v0.9.4
AutoConnectAux    Timezone;

//wifi and device on Thingsboard
//#define WIFI_AP "tollieollie"
//#define WIFI_PASSWORD "Jaketom5"
//#define TOKEN "A1_TEST_TOKEN"    //Dev board
#define TOKEN "ecg_spaches"      //Prototype
char thingsboardServer[] = "134.129.122.213";
WiFiClient wifiClient;
ThingsBoard tb(wifiClient);
int status = WL_IDLE_STATUS;
unsigned long lastSend;

//NTP library to get real time from server
#define NTP_OFFSET   0 * 60      // In seconds
#define NTP_INTERVAL 5 * 1000    // In miliseconds
#define NTP_ADDRESS  "pool.ntp.org"
WiFiUDP ntpUDP;
NTPClient timeClient(ntpUDP, NTP_ADDRESS, NTP_OFFSET, NTP_INTERVAL);


//timestamp variables
unsigned long long timestamp;
unsigned long long real_time;
unsigned long long previous_ts;
int ii = 0;

//LED Time Variables
unsigned long current_time_LED;
unsigned long previous_time_LED;
unsigned long elapsed_time_LED = 0;
float voltage = 0.0f;
float percentage = 0.0f;
int battStatus = 5; //Start in default mode (not transmitting)
int ledState = LOW;   // ledState used to set the LED

//Packet format
#define  CES_CMDIF_PKT_START_1      0x0A
#define  CES_CMDIF_PKT_START_2      0xFA
#define  CES_CMDIF_TYPE_DATA        0x02
#define  CES_CMDIF_PKT_STOP_1       0x00
#define  CES_CMDIF_PKT_STOP_2       0x0B
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
